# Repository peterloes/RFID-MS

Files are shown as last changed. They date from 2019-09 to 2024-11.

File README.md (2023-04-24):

# RFID Management System RFID-MS
 
Authors: Loës P., Skripsky P., Kempenaers B. (2019) 

### Platform for animal observation 

An efficient system to monitor animal behaviour in wildlife
as well as in laboratory settings.

-	Compatible with different RFID systems and triggers
-	Low power consumption and specific data collection lead to long lasting collection periods
-	Applicable world-wide due to its compatibility with different types of radio clock receivers 
-	High observation quality through low disturbance of the animals

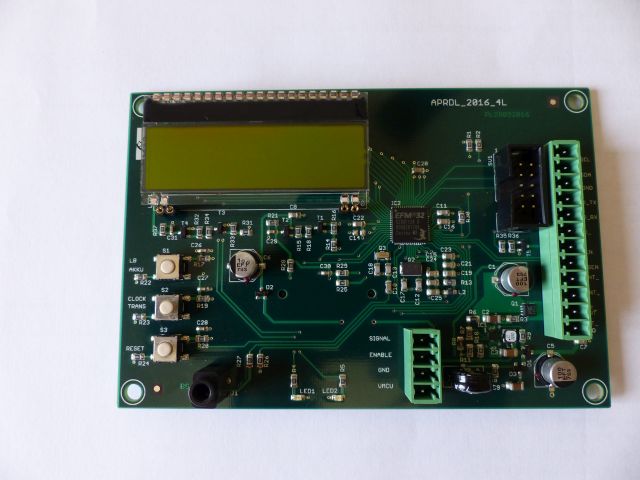
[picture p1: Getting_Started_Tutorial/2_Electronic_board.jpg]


- Time Synchronization with atomic clock once a day to ensure optimal data quality
- Current Control twice a day
- Forecast for Battery-Change implemented
- Energy Bypass so that Date and Time are maintained even when changing battery
- Hyperterminal Output to get real-time data to the computer/laptop
- Low-Power Device:sleep: 40µA@12V awake: 12mA@12V

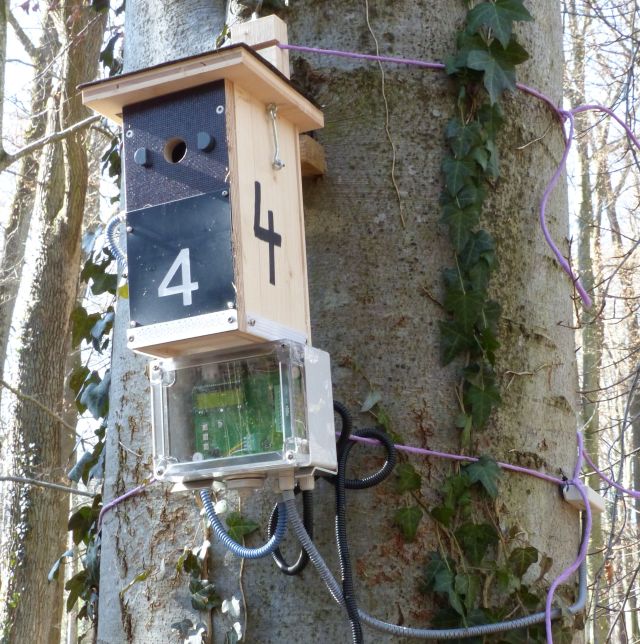
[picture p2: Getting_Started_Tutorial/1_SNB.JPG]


SmartNestBox Application:

https://github.com/peterloes/RFID-MS/blob/master/Getting_Started_Tutorial/1_poster_overview_2.pdf

Raw data on SD Card:

https://github.com/peterloes/RFID-MS/blob/master/Getting_Started_Tutorial/6_rawdata_BOX0001.TXT

Optional components:

https://github.com/peterloes/Light_Barrier

https://github.com/peterloes/Booter_RFID-MS_MOMO_TAMDL

https://github.com/peterloes/Clock_receiver_RFID-MS_MOMO_TAMDL

Manufacture:

https://github.com/peterloes/RFID-MS/blob/master/Getting_Started_Tutorial/5_Supplier.txt

C is the Greenest Programming Language

To achieve its power and energy-efficiency features, EFM32 products utilize ultralow active and idle power,
fast wakeup and processing times, and most important, the ability to intelligently interact with peripherals
and sensors autonomously without waking up the CPU and consuming more power.

[\[paper\]](https://www.sciencedirect.com/science/article/pii/S0003347223000258?via%3Dihub)
Data on the Start and End of Activity.
All 277 nestboxes were equipped with a monitoring system that
automatically recorded each nestbox visit of a PIT-tagged individual.

https://www.mpg.de/14346664/0113-verh-060830-first-come-first-bred

https://www.mpg.de/14345523/0113-verh-060830-wer-zuerst-kommt-bruetet-zuerst

EXTENSION:

Smart nest-box with long range RFID reader and external light barrier.

https://github.com/peterloes/RFID-MS/blob/master/Getting_Started_Tutorial/3_SNB_LR_LB.jpg

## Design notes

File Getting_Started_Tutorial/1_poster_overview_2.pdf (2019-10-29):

### Radio frequency identification (RFID) Management System

A Novel Technology for Collecting Animal Behavioural Data

Peter Loës & Peter Skripsky Department Kempenærs

Max-Planck-Institut
für Ornithologie

8,3 mm

Standard recording (bird entering nest box):

20190122-170542.326 LBO:ON 20190122-170542.326 RFID is powered ON 20190122-170542.484 LBI:ON 20190122-170542.670 Transponder: 6140000000008001
20190122-170543.870 LBO:off 20190122-170543.924 LBI:off 20190122-171143.000 RFID is powered off

RFID tag/transponder:

Uses of the APRDL:
- Reproductive behavior (e.g. incubation and brooding rates, feeding rates, etc.)
- Individual dispersal for adults and fledglings
- Survival or return rates
- Breeding site selection
- Social interactions (e.g. social networks at feeders)

Benefits of using APRDL over traditional methods

(visual observations and camera traps):
- No observer biases and not affected by low visibility
- Autonomous – requires minimal battery and SD card changes
- Only active during events (e.g. bird entering a nest box) → does not need time-consuming processing like camera traps
- Allows for 24/7 data collection, and large data sets with high accuracy
- Compatible with any species that can be equipped with a RFID tag

Specifications:
- Low power device → inactive current mode = 40µA (0,040mA)
- Useful for wild populations and laboratory experiments
- Compatible with different RFID readers and external triggers (Light barriers or infrared detectors)
- Can be used with different radio clock receivers (e.g. Germany 77,5 kHz, UK and USA 60 kHz, and China 68,5 kHz)
- Reliable in harsh environments (-40°C – 60°C)
- Used with Short Range readers (3,3V@0,22A)
- 12V battery pack

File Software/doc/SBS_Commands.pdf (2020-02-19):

# Projekt U-BMS2-4

# SBS-

# Commands

# SBS Commands

Device Address | | | | | | 0x0A
ManufacturerAccess | | | | | | 0x00

Read word

RemainingCapacityAlarm | 0x01

Read word
Rückgabe des remainingCapacityAlarm-Wertes in [mAh].

Wenn die Restkapazität(remainingCapacity) kleiner als der Wert vom RemainingCapacityAlarm ist, sendet die Batterie eine Alarmwarnung zum Host. Der RemainingCapacityAlarm-Flag im Battery-Status wird gesetzt.

RemainingTimeAlarm | 0x02

Read word
Rückgabe des remainingTimeAlarm -Wertes in [min].

Wenn die durchschnittliche Entladezeit des Akkus(AverageTimeToEmpty) kleiner als der Wert vom
RemainingTimeAlarm | ist, | sendet | die | Batterie | eine | Alarmwarnung | zum | Host. | Der
RemainingTimeAlarm-Flag im Battery-Status wird gesetzt.
Battery Mode | | | | | | 0x03

Read word

Bit | Beschreibung

### 12 BALANCING CELL3

### 11 BALANCING CELL2

### 10 BALANCING CELL1

### 6 BALANCING CELL4

### 5 Deep Under Voltage recovery(DUVRD) Bit vom FET Control and Status-Register

(FCSR)

### 4 Current Protection Status (CPS) Bit vom FET Control and Status-Register (FCSR)

### 3 Discharge FET (DFE) Bit vom FET Control and Status-Register (FCSR)

### 2 Charge FET (CFE) Bit vom FET Control and Status-Register (FCSR)

CoreTemperature | 0x08

Read word
Die aktuelle Chip-Temperatur in [°K]
Voltage | 0x09

Read word
Die gesamte Akkuspannung in [mV]
BatteryCurrent | 0x0A

Read word
Der aktuelle Strom in [mA], der aus bzw. in den Akkupack durchfließt.
BatteryAverageCurrent | 0x0B

Read word
Der durchschnittliche Strom des Akkupacks in [mA]
RelativeStateOfCharge | 0x0D

Read word
Der relative Ladezustand des Akkupacks in [%]
AbsoluteStateOfCharge | 0x0E

Read word
Der absolute Ladezustand des Akkupacks in [%]
RemainingCapacity | 0x0F

Read word
Die Restkapazität des Akkupacks in [mAh]
FullChargeCapacity | 0x10

Read word
Rückgabe der vollen Ladekapazität in [mAh]
RunTimeToEmpty | 0x11

Read word
Die Ladezeit in [min]
AverageTimeToEmpty | 0x12

Read word
Die durchschnittliche Entladezeit [min]
AverageTimeToFull | 0x13

Read word
Die durchschnittliche Ladezeit in [min]

ChargingCurrent | 0x14

Read word
Der Ladestrom in [mA]
ChargingVoltage | 0x15

Read word
Die maximale Ladespannung in [mV]
Battery Status (flags) | 0x16

Read word

Bit | Beschreibung

### 15 Over Charged Alarm

Überprüfung des chargingProhibited-Flags

### 14 Terminate Charge Alarm

Überprüfung des voltageTooHigh-Flags

### 12 Over Temp Alarm

Überprüfung des cellTemperatureTooHigh -Flags

### 11 Terminante Discharge Alarm

Dieses Bit wird gesetzt, wenn die Restkapazität unter dem definierten Wert von SBS_TERMINATE_DISCHARGE_LIMIT (Standard 5mAh) liegt. Wenn ein Ladegerät erkannt wird, wird dieses Bit gelöscht.

### 10 Battery Protection Triggered

Dieses Bit wird gesetzt, wenn die Batterieschutz-Hardware die FETs ausschaltet.

### 9 Remaining Capacity Alarm

Dieses Bit wird gesetzt, wenn die Restkapazität weniger als der definierte Wert des Restkapazität-Alarms(RemainingCapacityAlarm) ist.

### 8 Remaining Time Alarm :

Wenn die durchschnittlische Entladezeit (AverageTimeToEmpty) kleiner als der definierte Wert des Entladezeit-Alarms (RemainingTimeAlarm) ist, wird dieses Bit gesetzt.

### 7 Initialized

Dieses Bit wird gesetzt, wenn die Initialisierung erfolgreich abgeschlossen ist.

### 6 Discharging

Dieses Bit wird gesetzt, wenn ein Entladestrom fließt.

### 5 Fully Charged

Dieses Bit wird gesetzt, wenn die Batterie vollständig geladen ist. Wenn ein Entladestrom aus der Batterie fließt, der höher als der Standby-Stromwert ist, wird dieses Bit gelöscht.

### 4 Fully Discharged

Dieses Bit wird gesetzt, wenn die Restkapazität der Batterie bzw. die Zellenspannung sehr niedrig ist. Wenn der relative Ladezustand über 20% steigt, wird dieses Bit gelöscht.

ChargerCycleCount | 0x17

Read word
Die Anzahl der Ladezyklen
DesignCapacity | 0x18

Read word
Die Nennkapazität in [mAh]
DesignVoltage | 0x19

Read word
Die Nennspannung in [mV]
SpecificationInfo | 0x1A

Read word
Die Spezifikation-Info (Version und Revision-Nummer)
ManufactureDate | 0x1B

Read word
Das Herstellungsdatum
SerialNumber | 0x1C

Read word
Die Seriennummer
ManufacturerName | 0x20

Read Block
Der Name des Herstellers
DeviceName | 0x21

Read Block
Der Name des Gerätes
DeviceChemistry | 0x22

Read Block
Die chemische Bezeichnung des Gerätes
ManufacturerData | 0x23

Read Block
Die Herstellerdaten
ShuntResistance | 0x2A

Read word
Der Wert des Shunt-Widerstands in [µOhm]

CellsInSeries | 0x3C

Read word
Anzahl der verwendeten Zellen in Serie
OverCurrentReactionTime | 0x3D

Read word
Überstrom Reaktionszeit Stufe 1
OverCurrentCharge | 0x3E

Read word
Überladestrom Stufe 1
OverCurrentDischarge | 0x3F

Read word
Überentladestrom Stufe 1
HighCurrentReactionTime | 0x40

Read word
Überstrom Reaktionszeit Stufe 2
HighCurrentCharge | 0x41

Read word
Überladestrom Reaktionszeit Stufe 2
HighCurrentDischarge | 0x42

Read word
Überentladestrom Stufe 2
VoltageCell4 | 0x44

Read word
Rückgabe der Spannung der Zelle 4 in [mV]
VoltageCell3 | 0x45

Read word
Rückgabe der Spannung der Zelle 3 in [mV]
VoltageCell2 | 0x46

Read word
Rückgabe der Spannung der Zelle 3 in [mV]

VoltageCell1 | 0x47

Read word
Rückgabe der Spannung der Zelle 1 in [mV]
CellMinVoltage | 0x54

Read word
Die minimale Zellenspannung in [mV]
CellMaxVoltage | 0x55

Read word
Der Wert der maximalen Zellenspannung in [mV]
CellPowerOffVoltage | 0x55

Read word
Der Wert der Zellenspannung in [mV], bei der das BMS in den PowerOffModus geht

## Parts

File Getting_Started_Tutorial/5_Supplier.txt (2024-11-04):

Active antennas
DCF77 Empfänger AASV DCFn PON/Ri/1m Aktivantenne SV DCFn 

HKW-Elektronik GmbH
Jörg Schneider

Eisenacher Str. 42 b
99848 Wutha-Farnroda / Thür.
Germany
Phone:  +49 (0)36921 3080 130
mailto:    schneider@hkw-elektronik.de
www.hkw-elektronik.de

Lightbarriers for front plate nestbox
Doppel - Lichtschranke Art.Nr. P00700 (Lichtschranken in Frontplatten):

SWISSSENSOR AG
Geschäftsleitung Hermann Beer

Steinacherstrasse 4
CH-9327 Tübach
Germany
Tel. +41(0)71 845 24 24
mailto:beer@swisssensor.ch
www.swisssensor.ch

Lithium Ionen rechargeable battery pack
Art.Nr. 60.16294 Panasonic NCR 18650GA 4S2P
14,4Volt 6900mAh inklusive SMBus Kabel je. 150mm 

DYNAMIS Batterien GmbH
Josef Pfeil

Brühlstraße 15  D- 78465 Dettingen / Konstanz
Tel. +49 (0) 75 33/93 669-15
mailto:josef.pfeil@dynamis-batterien.de
www.dynamis-batterien.de

RFID reader
Nanomodule Multi 125LV A/1.11 (T3NM-LV) 125kHz +/-0,5% Art.Nr. ART10413
ANT002 Rundspule 47mm, 490µH Art.Nr. ART 10668

Elatec GmbH
Felix Ellspermann

Zeppelinstr. 1
82178 Puchheim 
Germany
Tel: +49 89 552 9961 120
mailto: f.ellspermann@elatec.com
www.elatec-rfid.com

Small sized transponder, not uniqued.
GlassTag 1,41x8,3mm EM4305 134kHz

Programming required for transponders.

Rasmus Forntheil
Product Manager Animal ID
RBIS Europe, Smartrac Specialty GmbH

e: rasmus.forntheil@eu.averydennison.com
t: +49 (0) 2265 9919-14  |  m: +49 (0) 173 5688184
Gewerbeparkstr. 10, 51580 Reichshof-Wehnrath, Germany

Internet: https://www.averydennison.com/en/home.html

Supplier of all Electronic Boards

Top-Print Electronic GmbH
Oskar Schmid

Rosenheimer Landstr. 129a
85521 Ottobrunn
Germany
Tel.: +49-89-60668047
Fax: +49-89-60668049
mailto: info@top-print.eu
https://www.leiterplatten-muenchen.de/

Protective coating with Schmelzharz Bectron MR3404

KC – Kunststoff- Chemische Produkte GmbH
Holger Sarau-Burghardt

Leonberger Straße 86 
DE 71292 Friolzheim
phone: +49 (0)7044 9425 13
e-mail: h.sarau-burghardt@kc-produkte.com
http: www.conformalcoating.de

Industrial SD Cards ATP 2GB
https://www.atpinc.com/products/industrial-sd-cards

FTDI Chip cable (3.5mm Audio Jack to USB)
TTL-232R-3V3-AJ

Housing
https://www.spelsberg.de/industrieleergehaeuse/glatt-mit-befestigungsnocken/20100701/
TG PC 1612-9-to
Artikelnummer: 20100701 | Maße: 162 x 122 x 90 mm
Leergehäuse IP66 / IP67 Polycarbonat

Docklight RS232 Terminal / RS232 Monitor
https://docklight.de/information/

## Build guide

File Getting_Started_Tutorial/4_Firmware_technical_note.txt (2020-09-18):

APRDL (code name SNB_Heaven) is an application to control an intelligent
nest box (SNB = Smart Nest Box).  It consists of the following components:

APRDL_2020

Version 1.2
- Added support for battery controller TI bq40z50.
  LogBatteryInfo: Removed SBS_ManufacturerData.
  Display SBS_RunTimeToEmpty in days/hours/min.
  Display SBS_SerialNumber as hex value.
- Corrected decoding of Short-Range(SR) RFID Reader transponder ID
- Added Power Fail Logic
- Added Interrupt Priority Settings

Version 1.1

- ExtInt.c - External interrupt handler.
- Keys.c - Key interrupt handling and translation.
- AlarmClock.c - Alarm clock and timers facility.
- DCF77.c - DCF77 Atomic Clock Decoder
- clock.c - An implementation of the POSIX time() function.
- LCD_DOGM162.c - Driver for the DOGM162 LC-Display.
- Display.c - Display manager for LCD.
- LightBarrier.c - Interrupt logic for the outer and inner light barrier,
  enables the RFID reader.
- RFID.c - RFID reader to receive transponder IDs.
- BatteryMon.c - Battery monitor, periodically reads the state of the
  battery via the SMBus.
- LEUART.c - The Low-Energy UART can be used as monitoring and debugging
  connection to a host computer.
- microsd.c - Together with the files "diskio.c" and "ff.c", this module
  provides an implementation of a FAT file system on the SD-Card.
- Logging.c - Logging facility to send messages to the LEUART and store
  them into a file on the SD-Card.

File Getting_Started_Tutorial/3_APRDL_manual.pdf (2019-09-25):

## Max-Planck-Institut für Ornithologie

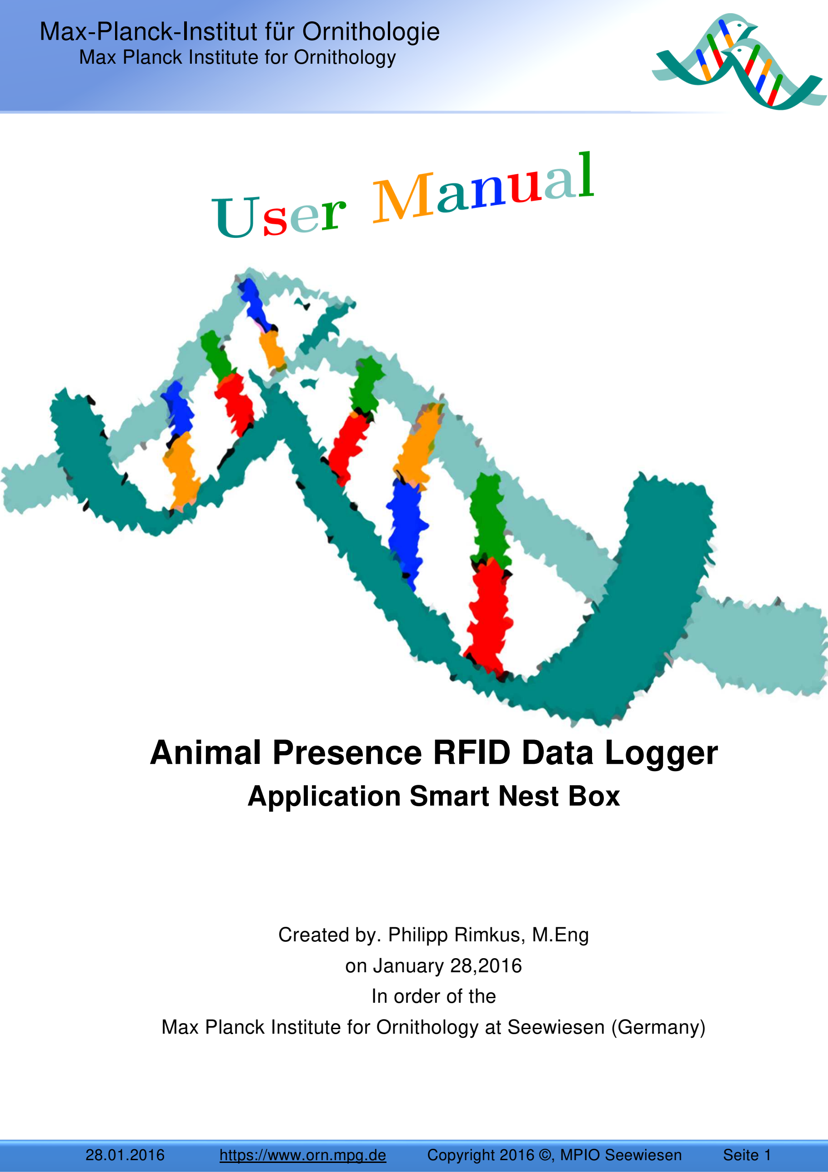
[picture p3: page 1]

Max Planck Institute for Ornithology

28.01.2016 | https://www.orn.mpg.de | Copyright 2016 ©, MPIO Seewiesen | Seite 1

# Animal Presence RFID Data Logger

## Application Smart Nest Box

Created by. Philipp Rimkus, M.Eng on January 28,2016
In order of the
Max Planck Institute for Ornithology at Seewiesen (Germany)

Disclaimer und Copyright

28.01.2016 | https://www.orn.mpg.de | Copyright 2016 ©, MPIO Seewiesen | Seite 2

## Disclaimer

The Animal Presence RFID Data Logger is to be used only as that described in this document. Any other method of usage is not permitted. If damage occurs due to incorrect usage, the manufacturer of the Animal Presence RFID Data logger is not liable.

## Copyright ©

The Copyright for this user manual remains with the manufacturer. Text and figures meet the latest technical status at the time of publication. Subject to change. The content of the user manual shall not affect any claims of the purchaser. The editor also welcomes suggestions of any possible improvements you may have or whether any errors are encountered.

Abkürzungsverzeichnis

28.01.2016 | https://www.orn.mpg.de | Copyright 2016 ©, MPIO Seewiesen | Seite 3

## List of abbreviations

SNB | Smart Nest Box
LBO | Light Barrier Outer
LBI | Light Barrier Inner
RFID | radio-frequency identification
EFM | Energy Friendly Microcontroller
PCB | printed circuit board
DCF | D for Deutschland (Germany), C for long-wave transmitter, F due to the vicinity to the Town Frankfurt
LCD | Liquid Crystal Display
ARM | Advanced RISC Machines
SD-CARD | Secure Digital Memory Card
PIT | Passive Integrated Transponder
LEUART | Low Energy Universal Asynchronous Receiver/Transmitter
USB | Universal Serial Bus

System Overview

28.01.2016 | https://www.orn.mpg.de | Copyright 2016 ©, MPIO Seewiesen | Seite 4

## System Overview

## General Description of Functions

The Animal Presence RFID Data Logger has been developed to record the behaviour of animals. When animals are equipped with transponders, they can then be identified by a reading device. Every animal equipped with a transponder can be identified individually. Whenever the individual passes a short tube containing the RFID Reader, the transponder code, date and time are saved on a SD-card.

The Animal Presence RFID Data Logger is designed for flexible, mobile operation in field. Therefore, the Data Logger uses rechargeable lithium-ion batteries to supply the electrical energy.

The use of electronic devices in the field and nature requires special features in order to operate correctly. Special developments are needed in order to cope with changes in ambient temperature, humidity, pressure and when the electrical power grid is unavailable. However, such developments can be time-consuming and cost-intensive.

Video recordings and visual observations have long been used by biologists to document behaviour of animals at their nests, and answer questions about territory, distribution and reproductive behaviour. However, these methods are time consuming, often inexact, and cannot be used when visibility is low (e.g. at night).

In a population of animals tagged with RFID devices the Animal Presence RFID Data Logger (APRDL), can detect, record and identify different individuals. This technology can be used for any species as long as the RFID tag (which is similar in size to a grain of rice) can be attached to the animal. The APRDL can be placed in any area where individuals are expected to frequent, such as a food source, nest or roosting area.

One major application of the APRDL is the Smart Nest Box, which is a wooden structure used by birds to rear their young. The APRDL records the presence of RFID-tagged adults, providing data on questions on many aspects of reproductive behaviour, including nest site selection, incubation and feeding behaviours. If the young are also equipped with RFID tags, behaviour, fledging data and movement in an out of the nest can also be recorded.

System Overview

28.01.2016 | https://www.orn.mpg.de | Copyright 2016 ©, MPIO Seewiesen | Seite 5

A key strength of the APRDL is that it runs autonomously, and requires only periodic battery and memory card changes. This allows for data collection over long periods of time with little effort, making the APRDL ideal for use in remote areas. It also allows data to be collected simultaneously at many sites without requiring the presence of a technician. During the development, special attention was paid developing an energy saving operation, so that a battery pack would only have to be changed every two weeks during periods of very high activity levels of the Animal Presence RFID Data Logger. The SD cards used have enough memory space to save data for several months of data collection. These low operating expenses makes the Animal Presence RFID Data Logger ideal for use in isolated locations without grid connection.

Another strength of the APRDL is how the data is recorded: the output of the APRDL is only the events (e.g. the time, date, and the individual present). This output is simple to work with, and does not require time-consuming processing, unlike video recordings where each video must be watched in order to document events. Thus the APRDL allows for easy collection of large amounts of data, making it easier to increase sample size with lower effort and higher accuracy.

Biological data is optimally collected when disturbance to the animal’s behaviour is minimised. As the APRDL is automated and requires only occasional battery and SD card changes, large volumes of data can be collected with little disturbance. It is also more accurate than many other methods of recording animal presence and identifying individuals, such as re-sighting colour bands or other markings, as these methods are prone to mistakes caused by poor visibility and human error.

Currently, the APRDL is being used on animals smaller then 70mm, however this technology could be adapted for use in any animal that can be marked with an RFID and returns to a specific area where the reader is located.

Some examples of potential uses of the APRDL

- nest boxes of birds
- bird feeders
- roosting boxes of bats
- dens of burrowing mammals or birds (i.e. rodents, badgers, rabbits, sea-

birds)
- fish such as pacific salmon that return to a stream to breed
- fish farms

System Overview

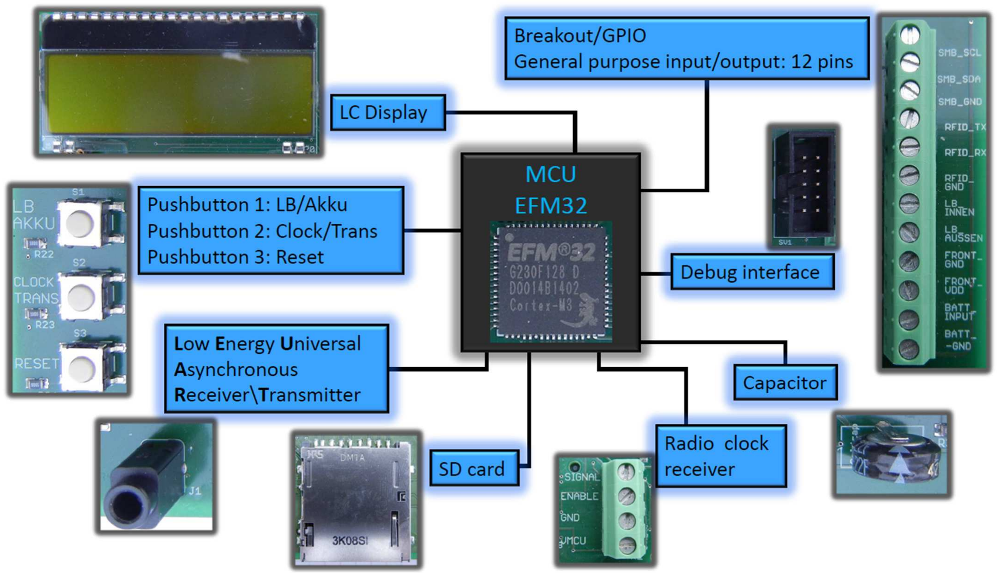
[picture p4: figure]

28.01.2016 | https://www.orn.mpg.de | Copyright 2016 ©, MPIO Seewiesen | Seite 6
- snake and reptile research
- bird movement and range

The APRDL can be used to collect data on many types of animal behaviour. Some of these include:

- Reproductive behaviours, such as incubation timing, feeding trips and the

duration of parental care.
- Dispersal and range size (the movement of animals within an area).
- Survival and return rates of individuals to an area.
- Selection of nesting or roosting locations

## System configuration main circuit board

The Smart Nest Box application of the Animal Presence RFID Data Logger was developed over several years. After five years of development a relatively reliable and efficient version was completed, which is described comprehensively in this manual. Additional detailed information, particularly concerning the electronic configuration, can be found in the datasheet for the Animal Presence RFID Data Logger.

### 1.2.1 Block diagram

System Overview

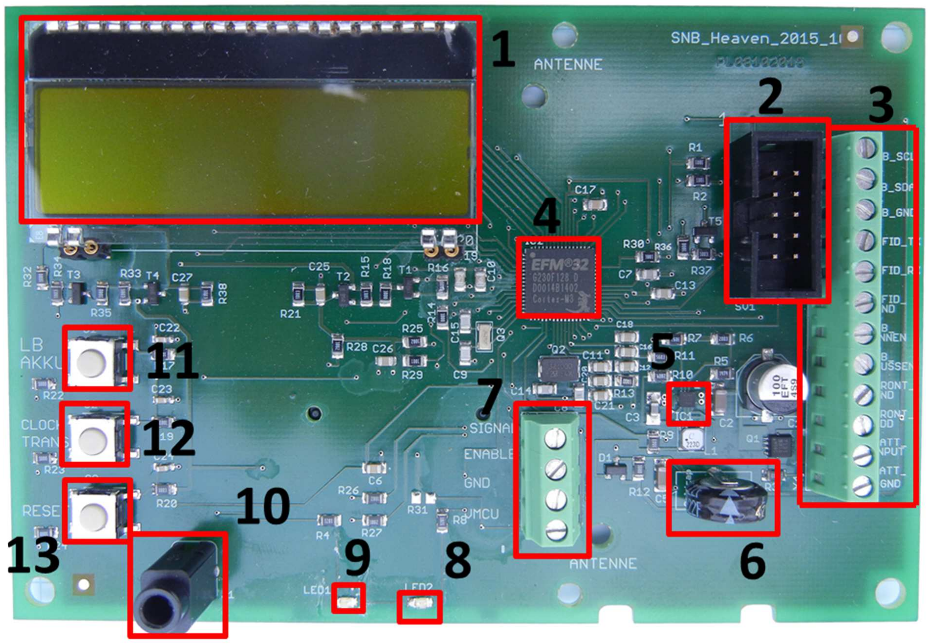
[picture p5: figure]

28.01.2016 | https://www.orn.mpg.de | Copyright 2016 ©, MPIO Seewiesen | Seite 7

### 1.2.2 Hardware Illustration

1. | LC Display | 8. | LED 2
2. | Debug interface | 9. | LED 1
3. | Connecting terminal for periphery | 10. | LEUART connector
4. | EFM32G230 | 11. | Pushbutton for battery indicator
5. | Down converter | 12. | Pushbutton for radio clock display
6. | Capacitor | 13. | Reset push button
7. Connecting terminal for the radio | clock

System Overview

28.01.2016 | https://www.orn.mpg.de | Copyright 2016 ©, MPIO Seewiesen | Seite 8

### 1.2.3 EFM32 microcontroller

A microcontroller is a small computer (SoC) on a single integrated circuit containing a processor core, memory, and programmable input/output peripherals. Program memory in the form of Ferroelectric
RAM, NOR flash or OTP ROM is also often included on the chip, as well as a typically small amount of RAM. Microcontrollers are designed for embedded applications, in contrast to microprocessors used in personal computers or other general purpose applications consisting of various discrete chips

The EFM32 MCUs by Energy Micro are the world’s most energy-friendly microcontrollers. With a unique combination of the powerful 32-bit ARM Cortex-M3, innovative low energy techniques, short wake-up time from energy saving modes, and a wide selection of peripherals, the EFM32G microcontroller is well suited for any battery operated application as well as other systems requiring high performance and low-energy consumption. EFM stands for Energy Friendly Microcontrollers. The ARM Cortex-M3 processor has several energy modes that can be quickly switched back and forth between them. It is possible to connect several peripheral devices. The ARM Cortex-M3 processor is developed by Energy Micro and has been bought by Silicon Labs.

Within the Animal Presence RFID Data Logger the EFM32G230 microcontroller is used with 128 KB Flash Memory, 16 KB RAM Memory and 32 MHz.

The EFM32 series is also known as “Gecko” by the developer, as these animals consume only 10% of the energy used by a mammal of similar size.

The EFM32 microcontroller based on the ARM Cortex processor is well suited for energy saving applications such as:

- Electricity-, gas- and water-meters
- factory automation and building automation systems
- alarm and security technology

System Overview

28.01.2016 | https://www.orn.mpg.de | Copyright 2016 ©, MPIO Seewiesen | Seite 9

Energy Micro states that benchmark measurements with other leading energy saving MCU’s, found that the EFM32-MCU consumes only a quarter of the energy consumed by the other 8-, 16-, or 32-bit-MCU’s.

The EFM32G230 contains a kind of UART-interface for communication with other systems, this is especially designed for energy saving. The interface is referred to as LEUART-interface. LEUART is a serial interface, a kind of bus system. Through the LEUART-interface, a jack connector and a USB cable can be used to establish a connection to a computer.

### 1.2.4 Debug Interface (DBG)

The debug interface software is stored on the microcontroller flash memory. Only after the flash memory contains this information, the hardware can be operated. The connection is either realised directly with a USB cable to the debug interface or with a debugging probe. If the connection is realized directly through the USB cable only HEX files and BIN files can be transferred.

### 1.2.5 Liquid Crystal Display (LCD)

This kind of display screen utilizes liquid crystals, which influence the polarization direction of light when a certain amount
of electrical voltage is applied.

LCD’s consist of segments which can independently change their transparency. This is done by a change in the orientation of each segment of the liquid crystals when an electrical voltage is applied. This then changes the permeability for polarized light, which is created by a
backlight.

In the Smart Nest Box application of the Animal Presence RFID Data Logger, the LCD shows the results depending on which buttons are pressed, as described in chapter 1.2.7.

System Overview

28.01.2016 | https://www.orn.mpg.de | Copyright 2016 ©, MPIO Seewiesen | Seite 10

### 1.2.6 SD Memory Card Connector

The data from the RAM memory is stored in form of TXT files on the SD-card, this is located in the SD Memory Card Connector. The size of the memory influences the energy consumption; the smaller the memory size is, the smaller the energy consumption. Therefore, it is recommended for the Animal Presence RFID Data Logger to use the smallest possible SD memory size of 2 GB. Memory sizes are supported from 2 GB to 32 GB.

### 1.2.7 Buttons

Three pushbuttons are installed on the mainboard of the Animal Presence RFID Data Logger. A LB Akku button, a Clock Trans button and a reset button

- LB Akku: Displays the status of the light barriers and

the status of the accumulator on the LCD.
- Clock Trans: Displays the date, time and the number of

the most recent transponder to enter the Smart Nest Box.
- Reset: Restarts the Animal Presence RFID Data Logger.

### 1.2.8 Capacitor

A capacitor (German “Kondensator”) is a passive electric component with the ability to store electrical charge and electrical energy in an electrical field.

When the electrical power supply through the accumulator for the Animal Presence RFID Data Logger
is missing, the capacitor ensures an alternate power supply. The capacitor is charged when the accumulator supplies energy to the system. This allows energy to be obtained for a certain time from the capacitor if it is required.

System Overview

28.01.2016 | https://www.orn.mpg.de | Copyright 2016 ©, MPIO Seewiesen | Seite 11

A Gold Cap is a double-layered capacitor, developed by Panasonic in 1972, then in 1978 it was brought released to the market. It is often known as “super cap” by a number of manufacturers. The name “Gold Cap” is the official trade name of the capacitor, trademarked by Panasonic. Cap is the shortcut for Capacitor. The gold refers to the gold plating of these capacitors. Gold is not contained in this capacitor.

The double-layered capacitor or Gold Cap is a mixture of a battery and a conventional capacitor. It combines speed and a large energy storage to form a super capacitor. With respect to its properties, it is ordered between electrolytic capacitors and rechargeable batteries.

Some applications only become possible through double layered capacitors. Despite its large capacity, it is very small in size. The dielectric strength is not exceptionally high however, with only a few volts. Through its large capacity, the Gold Cap is present to maintain the power supply when the main energy source fails. In devices in which data storage should remain in switched off status, the Gold Cap is particularly well suited.

Life expectancy is limited from roughly 8 to 10 years. When the operating temperature is above optimal or the discharge current is high, the life expectancy and the capacity begin to decline over time. The Gold Cap most appropriate when it is rarely discharged and used with low currents.

### 1.2.9 Jack connector as interface to a PC

For the development of the Animal Presence RFID Data Logger an Interface for connection to a computer is intended. Through the data communication interface LEUART, which is provided by the
EFM32G230 out of chapter 1.2.3.

The jack connector is used to interlink the signal from the LEUART interface with a computer. Specifically, a jack connector of 3.5 mm is used, as those used in many audio applications.

### 1.2.10 Down converter

The TPS62125 from Texas Instruments, is a high efficiency synchronous step down converter optimized for low and ultra-low power applications providing up to 300 mA output current. It has a wide range of input voltages, from 3V to 17V, sup-

System Overview

28.01.2016 | https://www.orn.mpg.de | Copyright 2016 ©, MPIO Seewiesen | Seite 12

ports four cell alkaline, and 1 to 4 cell Li-Ion batteries in series configuration as well as 9V to 15V powered applications. The device includes a precise low power enabled comparator which can be used as an input supply voltage supervisor (SVS), this addresses system specific power up and down requirements.

### 1.2.11 LED’s

The Animal Presence RFID Data Logger is equipped with two LED’s, one red and one orange. The orange LED (LED 2) indicates, that something is written on the SD card. If the red LED (LED 1) flashes, this indicates that the radio clock is transmitting a signal to the MCU. If the LED 1 blinks longer than 5 minutes or flashes continuously, this indicates a malfunction.

### 1.2.12 Connector for the peripherals

At the connector for the peripheral devices, devices such as a batteries, light barriers and RFID’s are connected here. The connected cables are collected and lead out of the housing in a cable conduit. A sealing against water and moisture is present here and very important.

## System configuration secondary board with radio clock

On the mainboard a secondary board is installed, this secondary board is attached by spacers. The antenna is located on the secondary board at the DCF77 receiver module . The distance between the DCF77 receiver module and the mainboard is necessary to improve the reception quality of the antenna.

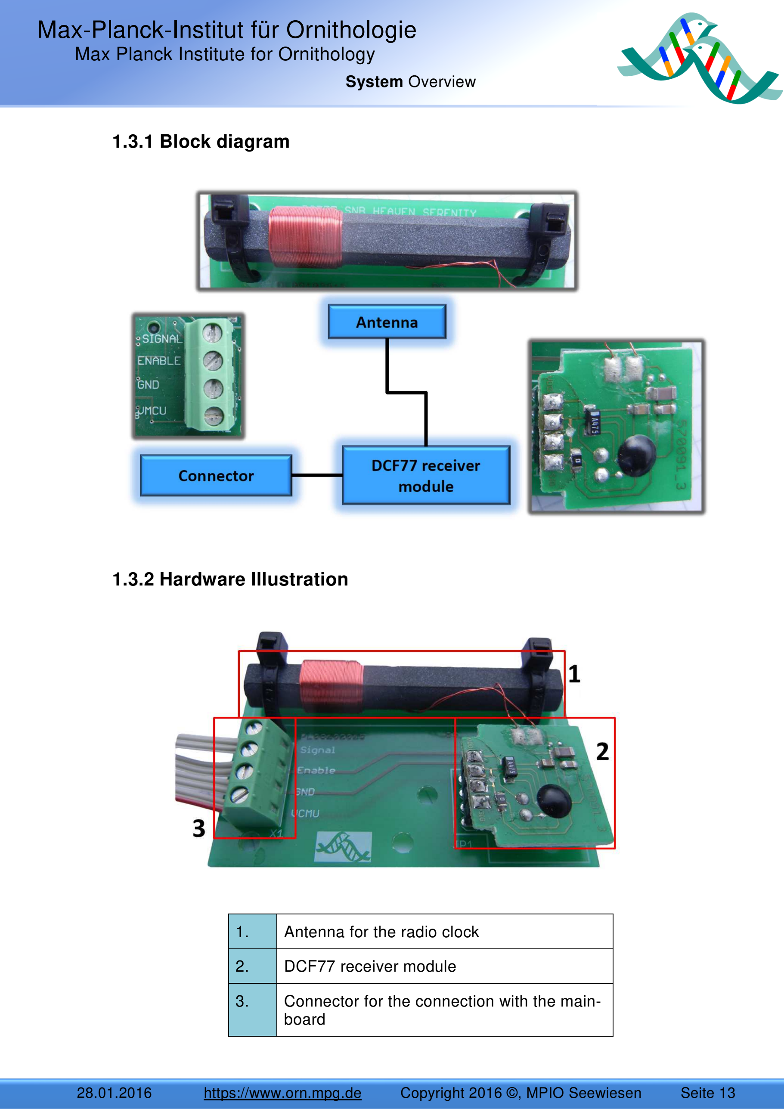
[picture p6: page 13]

System Overview

28.01.2016 | https://www.orn.mpg.de | Copyright 2016 ©, MPIO Seewiesen | Seite 13

### 1.3.1 Block diagram

### 1.3.2 Hardware Illustration

1. Antenna for the radio clock
2. DCF77 receiver module
3. Connector for the connection with the main- | board

System Overview

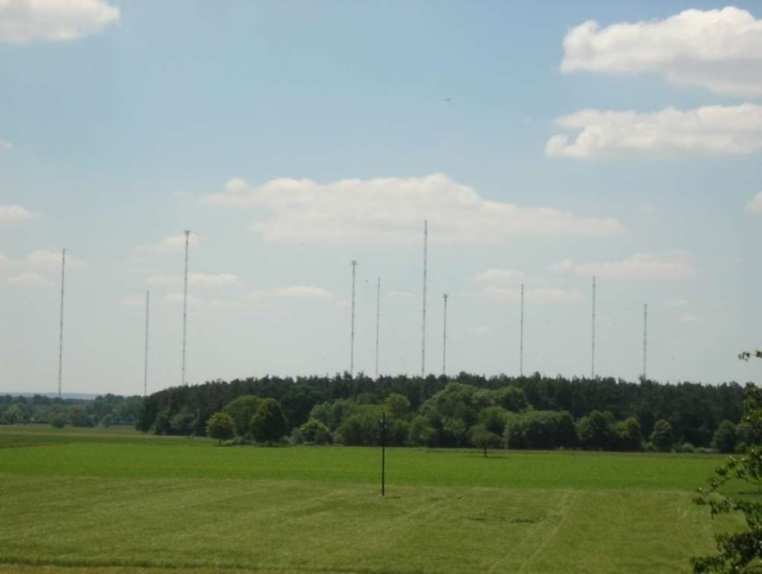
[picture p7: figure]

28.01.2016 | https://www.orn.mpg.de | Copyright 2016 ©, MPIO Seewiesen | Seite 14

### 1.3.3 Radio clock DCF (77.5KHz)

The current version of the Animal Presence RFID Data Logger features a radio clock, which works in a similar way as normal radio alarm clocks. In periodic intervals a signal to Europe from the long wave antenna in Mainflingen with a frequency of 77.5 kHz is received and synchronized. Long wave signals have been compared to short waves and medium
waves, and have a relatively high
range. So it is possible to receive
the signal from Mainflingen with a range up to 2000 km. In other continents the time signals can be also received, however with different frequencies. The radio clock is powered via an accumulator, which is also used for the other electrical consumers and is described in chapter 1.5.
countries | designation | frequency
Germany | DCF | 77.5 kHz
France | TDF | 162 kHz
China | BPC | 68.5 kHz
Japan | JJY | 40 und 60 kHz
USA | WWVB | 60 kHz
Russia | Beta | 25 kHz
England | MSF | 60 kHz

System Overview

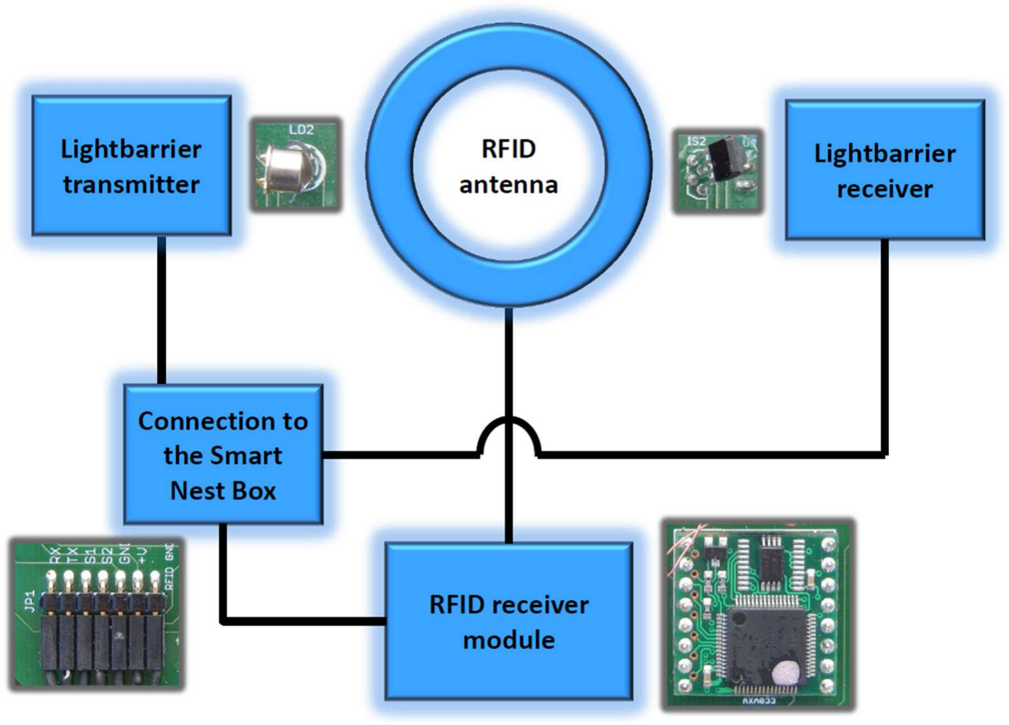
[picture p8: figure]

28.01.2016 | https://www.orn.mpg.de | Copyright 2016 ©, MPIO Seewiesen | Seite 15

## Peripheral equipment Smart Nest Box

Some peripheral devices are necessary for the operation of the Animal Presence RFID Data Logger with the Smart Nest Box application. These are the accumulator, two light barriers and an RFID reader.

### 1.4.1 Block diagram Smart Nest Box front panel

System Overview

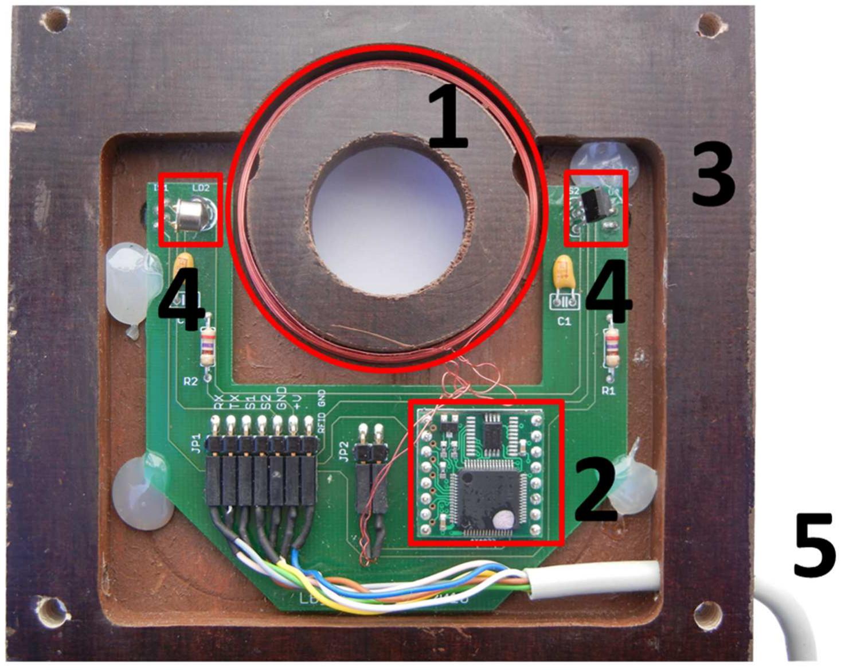
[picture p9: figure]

28.01.2016 | https://www.orn.mpg.de | Copyright 2016 ©, MPIO Seewiesen | Seite 16

### 1.4.2 Hardware illustration

The front panel may become damaged by squirrels, so much that the front panel had to be displaced. In recent versions the board and the antenna are sealed with plastic resins to avoid damages through oxidation.

1. Antenna with 70 mm diameter
2. RFID receiver module
3. Front panel of the Smart Nest Box con- | sisting of wood
4. Light barrier
5. Cable connection to the mainboard

System Overview

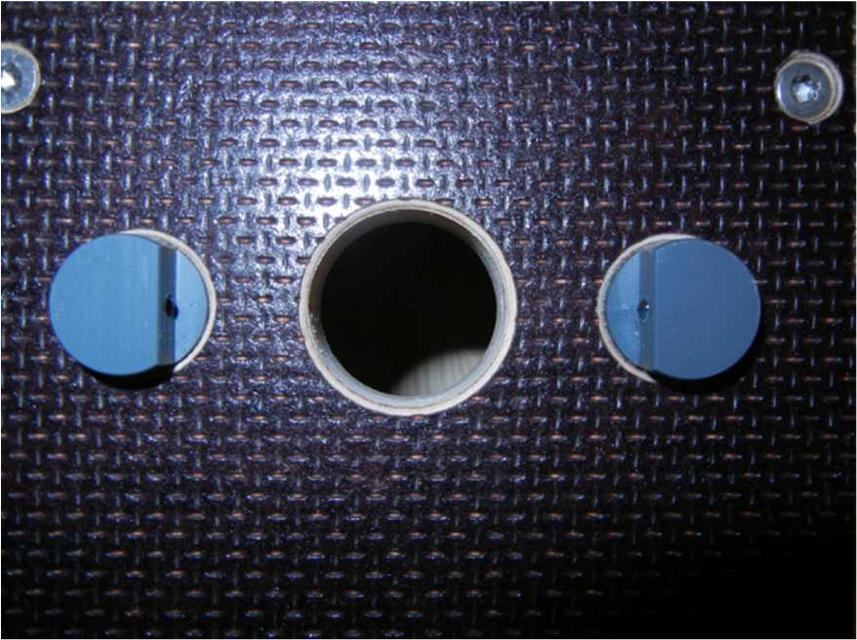
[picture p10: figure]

28.01.2016 | https://www.orn.mpg.de | Copyright 2016 ©, MPIO Seewiesen | Seite 17

### 1.4.3 Light barrier

A light barrier is an optoelectronics systems, these indicate an interruption in the beam of light and communicates this event through an electrical signal. Light barriers are composed of a beam source (transmitter) and a photodiode (emitter) to receive the beam.

In the Smart Nest Box application, the
light barriers detect the movements of the birds, including the direction of motion. On each side of the front panel there is one light transmitter and a light emitter, these detect the flight direction.

The light barriers can scan with a frequency of up to 100 Hz. The current consumption at 10 Hz is less than 30 µA (calculated). The covering of the light barriers is submitted through an
open collector output.

After the light barrier detects an object in the entrance of the Smart Nest Box, the RFID reader is activated. This needs to occur in a relatively short time, as often birds will fly very quickly through the entrance into the Smart Nest Box. If signal transmission is slower, the RFID can’t receive the transponder signal from the bird because the bird may already be out of range.

The light barriers work with adaptive selectivity, which means that pollution of the transmitter and emitter, aging or fluctuations due to temperature can be largely compensated for. This reduces the possibility of false detections for example through sunlight.

### 1.4.4 RFID

Radio-frequency identification (RFID) uses electromagnetic fields to automatically identify and track transponders attached to objects. The transponders contain electronically stored information. Passive transponders collect energy from a nearby RFID reader's interrogating radio waves. Active transponders have a local power source such as a battery and may operate at hundreds of meters from the

System Overview

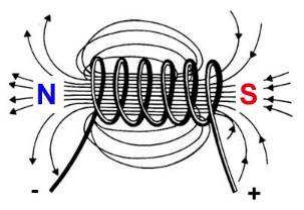
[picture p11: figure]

28.01.2016 | https://www.orn.mpg.de | Copyright 2016 ©, MPIO Seewiesen | Seite 18

RFID reader. Unlike a barcode, the transponder does not need to be within the line of sight of the reader, so it may be embedded within the tracked object.

RFID’s are also used in other areas such as electronic locks, ski passes, cashless payment transactions, electronic immobilizers and in libraries as theft protection.

In the Smart Nest Box application of the Animal Presence RFID Data Logger the transponder frequency is not exactly the same as the RFID reader frequency. The RFID Reader works with a frequency of 125 kHz and the transponder with 134.2 kHz. However, both systems are compatible and function together.

### 1.4.4.1 RFID receiver module

A RFID receiver module with a frequency of 125 kHz is used in the application Smart Nest Box. The used receiver module from Elatec is designed with a small size, small price and versatile applications.

### 1.4.4.2 RFID antenna 490µH

The used antenna has a diameter of 70 mm and is directly soldered on the RFID reader. If a voltage source is connected to the antenna, which is an air core coil and current begins to flow, an electric field is generated. The electric field is the energy source for the transponder.

If a transponder with its own antenna transmits a signal at a certain frequency, the RFID reader’s antenna collects the signal and the RFID reader transmits it further to the MCU.

System Overview

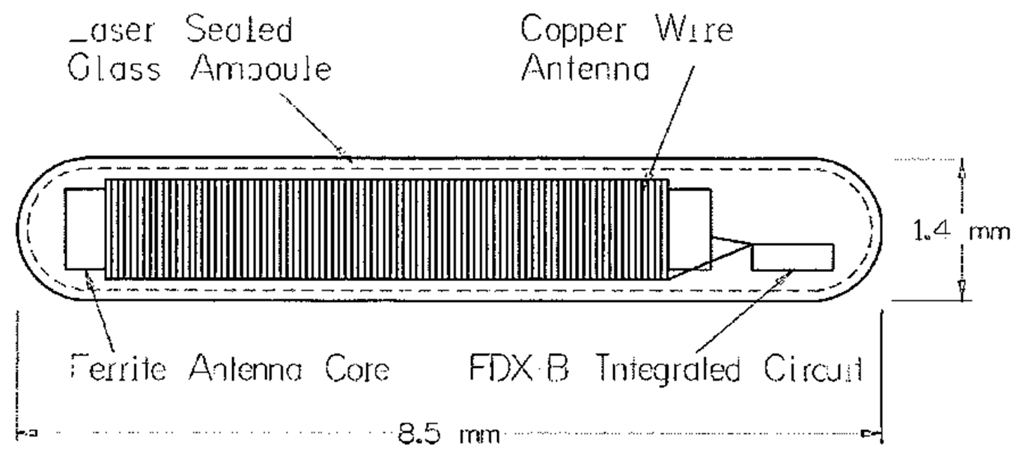
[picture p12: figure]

28.01.2016 | https://www.orn.mpg.de | Copyright 2016 ©, MPIO Seewiesen | Seite 19

### 1.4.4.3 RFID transponder

This is the highest performing RFID transponder on the market today for fish and wildlife research in an 8 mm 'skinny tag'. These transponders are encapsulated in biocompatible glass and provide 100% unique identification. Because of the small size of 8 mm x 1.4 mm
and a very low weight of only 30 mg the tagged animals are minimally affected. So it is possible to tag
even very small animals such as red ants.

The transponder contains a non-volatile flash memory. A combination of letters and numbers is stored on the flash memory during the production of the transponder.

The transponders are known as FDX-B
MINIHPT8 and are made by the company Biomark. The FDX-B indicates that the full duplex
technique is used.

In duplex mode operating systems the electric field is always present. The transponder sends its signal continuously as soon as it gets energy through the field and enters the reception area of the RFID reader. Therefore, the system works very rapidly.

System Overview

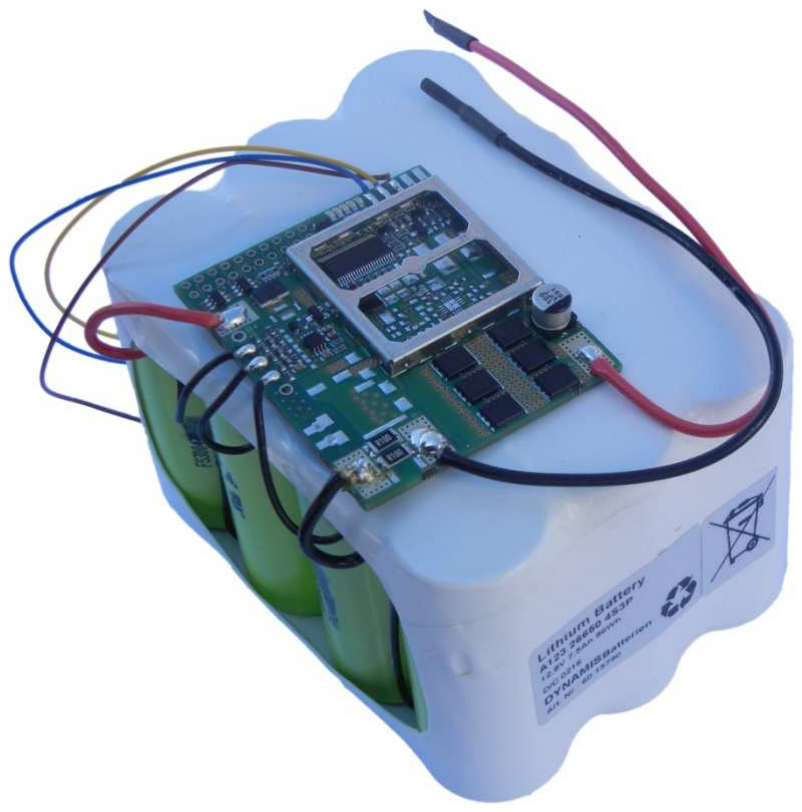
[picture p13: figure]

28.01.2016 | https://www.orn.mpg.de | Copyright 2016 ©, MPIO Seewiesen | Seite 20

## Accumulator

The lithium-ion battery from the company Dynamis Batterien supplies the Animal Presence RFID Data Logger with electrical energy. The amount of energy chosen was to ensure that there is
enough energy to supply the
Animal Presence RFID Data
Logger in a very active period for two weeks. Through the little specific energy of 108 Wh/kg the change of the accumulators is much less energy-sapping than with leadacid batteries with a specific energy of 30 – 40 Wh/kg.

The three LED’s on the accumulator’s board indicates the state of charge. One lit LED indicates that the accumulator is fully charged. Two
LED’s indicate the accumulator is halfway charged. Three
LED’s indicate an almost empty state of charge.

System Overview

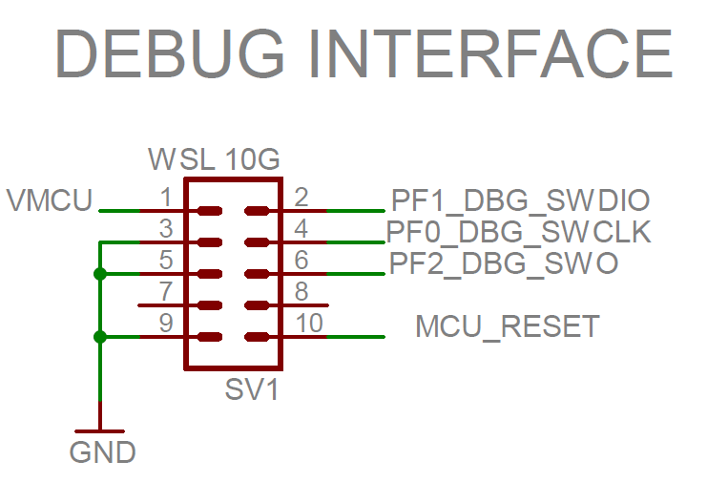
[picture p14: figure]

28.01.2016 | https://www.orn.mpg.de | Copyright 2016 ©, MPIO Seewiesen | Seite 21

## Pin assignment and connectors

### 1.6.1 Pins for debugging

### 1.6.2 Pin assignment

### 1.6.2.1 Energy supply connector

connection | designation
SV1-1 | VMCU
SV1-2 | SWDIO
SV1-3: | GND
SV1-4 | SWCLK
SV1-5 | GND
SV1-6: | SWO
SV1-7 | free
SV1-8 | free
SV1-9 | GND
SV1-10 | MCU_RESET
connection | designation | Cable color
X1-1 | BATT_GND | brown
X1-2 | BATT_INPUT | red
X1-3 | FRONT_VDD | white
X1-4 | FRONT_GND | brown
X1-5 | LB_AUSSEN | green
X1-6 | LB_INNEN | yellow
X1-7 | RFID_GND | blue
X1-8 | RFID_RX | grey

System Overview

28.01.2016 | https://www.orn.mpg.de | Copyright 2016 ©, MPIO Seewiesen | Seite 22

### 1.6.2.2 Connector for the radio clock

connection | designation
X2-1 | PD2_DCF77_Signal
X2-2 | PD1_DCF77_Enable
X2-3 | GND
X2-4 | VMCU
X1-9 | RFID_TX | pink
X1-10 | SMBUS_GND | grey
X1-11 | SMBUS_SDA | blue
X1-12 | SMBUS_SCL | yellow

System Overview

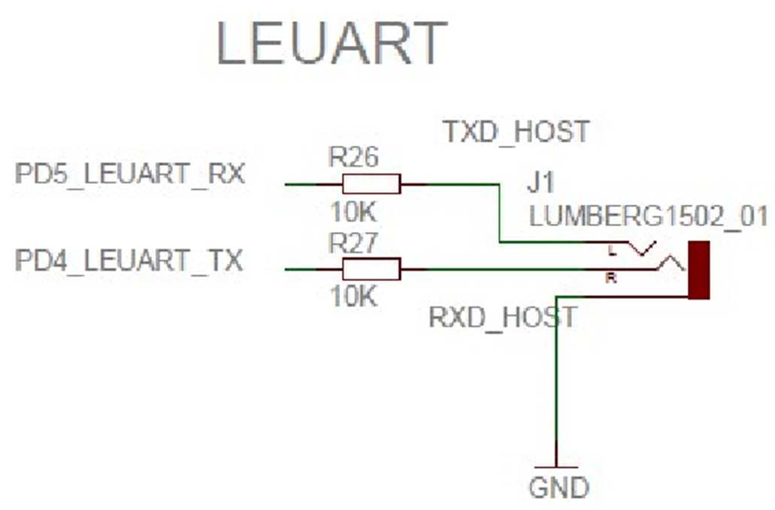
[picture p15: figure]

28.01.2016 | https://www.orn.mpg.de | Copyright 2016 ©, MPIO Seewiesen | Seite 23

### 1.6.2.3 Jack connectors for LEUART

## Housing

### 1.7.1 Housing for the main board

The housing from the main board consists entirely of opaque polycarbonate. The lid is lockable with bayonet locks which are quick and easy to use. The screws are secured from falling out and prevents loss of any screws.

connection | designation
J1 | LEUART_RX
J1 | LEUART_TX

System Overview

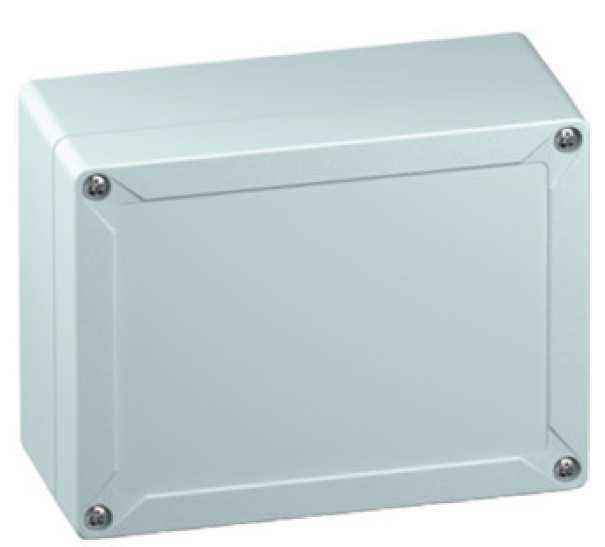
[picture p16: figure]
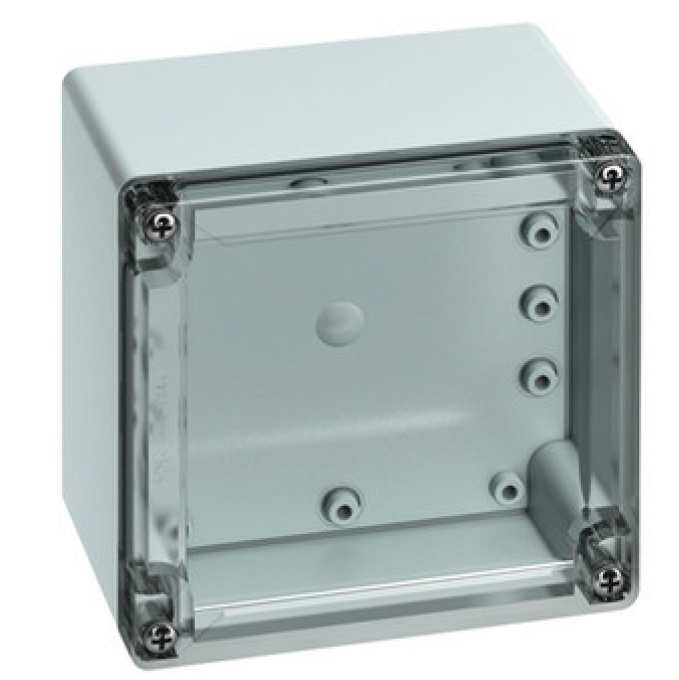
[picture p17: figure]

28.01.2016 | https://www.orn.mpg.de | Copyright 2016 ©, MPIO Seewiesen | Seite 24

### 1.7.2 Housing for the accumulator

The housing from the accumulator consists entirely of polycarbonate, with the lid being made from transparent polycarbonate so the LED’s inside may be seen without needing to open the lid. The lid is also lockable with bayonet locks. The same screws are used here and are also secured against falling out.

General working conditions

28.01.2016 | https://www.orn.mpg.de | Copyright 2016 ©, MPIO Seewiesen | Seite 25

## General working conditions

Component designation | Animal Presence RFID Data Logger
Manufacturer | MPIO http://www.orn.mpg.de/
Dimensions main board (L X B x H) | 121 mm x 81 mm x 1.5 mm
Overall temperature range | -10°C to 60°C (DCF77 and RFID) DCF is not absolutely essential -20°C to 60°C
Storage temperature range | -20°C to 60°C
Overall moisture | Relative moisture 35% to 85% (at 5°C to 35°C)

Detailed information, in particular information concerning the electrical properties can be found in the Animal Presence RFID Data Logger datasheet.

The working conditions from single devices can be found in the datasheets in chapter 7.

Energy supply

28.01.2016 | https://www.orn.mpg.de | Copyright 2016 ©, MPIO Seewiesen | Seite 26

## Energy supply

The Animal Presence RFID Data Logger is especially designed to have low energy requirements. The electrical power requirements are explained more precisely in this chapter.

The EFM32G230 has five different economical energy modes, where only two of which are used for the Animal Presence RFID Data Logger with the Smart Nest Box application. These are the Deep Sleep Mode and the Sleep Mode whereby the Sleep Mode is the Active Mode and the Deep Sleep Mode is the Inactive Mode. In these energy modes different consumers are active. The Smart Nest Box switches between the Active Mode and the Inactive Mode through light barrier activity. If the RFID reader and the light barrier detect no activity for 6 minutes the Smart Nest Box switches into the Inactive Mode again to save energy.

The energy-intensive consumers like the RFID reader are only supplied with electrical Energy when required. The RFID reader is the largest consumer of electrical energy in the Smart Nest Box application.

The electrical energy required is supplied by a lithium-ion-battery. If the energy demand and the energy storage capacity are known, the remaining range of the accumulator can be estimated.

In the following sections, the current supply and the voltage supply will be examined separately.

## Current supply

### 3.1.1 ARM Cortex Processor

From the five available modes of operation only the Deep Sleep Mode and the Sleep Mode are used.

Deep Sleep Mode or Inactive Mode

### 0.9 μA @ 3 V Deep Sleep Mode, including Real Time Clock with 32.768 kHz oscil-

lator, Power-on Reset, Brown-out Detector, RAM and CPU retention

Energy supply

28.01.2016 | https://www.orn.mpg.de | Copyright 2016 ©, MPIO Seewiesen | Seite 27

Sleep Mode or Active Mode

### 45 μA/MHz @ 3 V Sleep Mode

### 3.1.2 RFID reader

RFID on measured: 35.4mA

RFID off measured: 1.36mA

(From schematics)

### 3.1.3 Light barrier

The light barriers are always supplied with electricity independently from the two energy modes. To save energy, the status of the light barrier is not assessed continuously but 10 times per second thus with a frequency of 10 Hz. Therefore, one light barrier has a very small electrical energy demand of roughly 30 µA.

### 3.1.4 LC display

The LC display has no background light whereby results a low electrical energy demand of 0.500 mA when the LC display is switched on

If no button is pressed for 20 seconds, the LC display fades out.

Measured On 0.342mA | Measured Off: 0.016mA | (From schematics)

### 3.1.5 Radio Clock

The clock of the microcontroller is updated at a certain time in the night through the time signal DCF77 from Mainflingen. The time will be also updated when the Animal Presence RFID Data Logger is reset.

Nominal current 100µA | Quiescent current 5 µA

### 3.1.6 LED

Each LED has an electric current demand of 2 mA.

Energy supply

28.01.2016 | https://www.orn.mpg.de | Copyright 2016 ©, MPIO Seewiesen | Seite 28

### 3.1.7 Accumulator LED’s and self-discharge

LED‘s | electric current demand
Without LED | 271 µA
Only LED1 | 308 µA
LED1 + LED2 | 343 µA
LED1 + LED2 + LED3 | 384 µA

The self-discharge by lithium-ion-batteries at 20°C is less than 2% per month.

### 3.1.8 Overview of the nominal currents

This table contains the maximum current demands of the most important devices. If all are active at the same time the maximum current demand behind the down converter at 3,3 V is 51 mA and with that the power input of the Animal Presence RFID Data Logger with the Smart Nest Box application is around 0,1683 W.

devices | currents
RFID | 35.4 mA
LC display | 0.500 mA
2* LED | 2 x 2 mA
ARM Cortex M3 | 45 µA/MHz (1.44 mA)
Radio clock | 0.1 mA
Light barrier | 2 x 30 µA
Total current behind the down converter with 3.3V | 42.2 mA (When all consumers are active at the same time without down converter losses)
Total input in front of the down converter with 12.8 V | 155 mW (When all consumers are active at the same time with down converter losses)

Energy supply

28.01.2016 | https://www.orn.mpg.de | Copyright 2016 ©, MPIO Seewiesen | Seite 29

### 3.1.9 Overview of the currents in the different operating modes

| Shutoff Mode | Stop Mode | Deep Sleep | Sleep Mode | Run Mode
RFID | Not used | Not used | off | Can be on | Not used
ARM Cor-tex M3 | Not used | Not used | On | On | Not used
LCD | Not used | Not used | Can be on | Can be on | Not used
Radio clock | Not used | Not used | Can be on | Can be on | Not used
LED’s | Not used | Not used | Can be on | Can be on | Not used
Light bar-rier | Not used | Not used | On | On | Not used
Down converter | Not used | Not used | On | On | Not used
Accumu-lator board | Not used | Not used | On | On | Not used

Energy supply

28.01.2016 | https://www.orn.mpg.de | Copyright 2016 ©, MPIO Seewiesen | Seite 30
| Deep Sleep Mode (Inactive Mode) | Sleep Mode (Active Mode)
RFID | 0 | An (35.4mA)
ARM Cortex M3 | 0.9 µA | 45 µA/MHz (1.44 mA)
LCD | 1.2 mA (if on) | 1.2 mA (if on)
Radio clock | 0.1 mA (once a day, take 5 min.; also at restart) | 0.1 mA (once a day, take 5 min.; also at restart)
LED | 2 mA (2 units; if on) | 2 mA (2 units; if on)
Light barrier | 30 µA (2 units) | 30 µA (2 units)
Down converter | 13 μA | 13 μA
Total current behind the down con-verter (without down converter losses and 3.3 V) | 0.0609 mA (2 x light barriers and und MCU | 36.88 mA (RFID active, MCU active, 2 x light barriers, down converter)
Total input behind of the down con-verter (without down converter losses and 3.3 V) | 0.0609 mA x 3.3 V = 0.000201 W = 201 x 10^-6 W | 36.88 mA x 3.3 V = 0.122 W
Total input in front of the down con-verter (with down converter losses and 12.8 V) | (with η = 50%) 0.000201W/0,5 = 0.000402 W = 402 x 10^6 W | (with η = 90%) 0.122 /0.9 = 0.136 W
Total current in front of the down converter (with down converter loss-es 12.8 V) (theoretical) | (with η = 50%) 0.0314 mA | (with η = 90%) 10.6 mA
Measured total current in front of the down converter (with down con-verter losses 12.8 V) (real) | 0.070 mA = real measured Inactive Mode (connected radio clock but inac-tive, controller in Deep Sleep Mode, Gold Cap, connected LED but off, buttons, down converter) | 12.3 mA = real measured Active Mode (connected radio clock but inactive, controller, LED con-nected but off, capacitor, with-out LCD, SD card, down con-verter, light barrier, RFID on)
Accumulator board with LED‘s cur-rent demand | (0.271 mA – 0.384 mA) | (0.271 mA – 0.384 mA)
Total current with accumulator board | 0.3024 mA – 0.4154 mA | 10.87 mA – 10.98 mA
Total Input ink. accumulator board with 12.8 V (theoretical) | 0.00387 W – 0.00532 W | 0.139 W – 0.141 W
Total Input with measured value + theoretically accumulator board de-mand with 12.8 V (real) | 0.004 W – 0.0058 W | 0.161 W – 0.162 W

Energy supply

28.01.2016 | https://www.orn.mpg.de | Copyright 2016 ©, MPIO Seewiesen | Seite 31

## Voltage supply

All consumers are supplied with 3.3 Volts which is produced by the down converter from the 12.8 Volts from the lithium-ion-accumulator. The minimum input voltage for the down converter is 5 Volts.

## Electrical energy storage

The main power supply is ensured by the lithium-ion-accumulator. If the accumulator is removed a capacitor can supply the Animal Presence RFID Data Logger for around 30 seconds.

### 3.3.1 Accumulator

If the whole capacity of a lithium-ionaccumulator is completely used it can have negative effects on the lifetime of the accumulator. Therefore, a certain percentage is not used. The accumulator of the Animal Presence RFID Data Logger uses 83% of the total capacity.

The lithium-ion-accumulator has its own board which is able to communicate with the Animal Presence RFID Data Reader via a data bus.

### 3.3.2 Capacitor

If the energy supply from the accumulator is no longer available, a capacitor with

### 0.22 farad supplies the Animal Presence RFID Data Logger for around 30 sec-

onds. During the discharge, the voltage declines from 3.6 Volts to 1.8 Volts. 1.8 Volts is the minimum working Voltage for the MCU.

### 3.3.3 Conversion loss

The accumulator provides electrical energy with a voltage of 12.8 Volts. The EFM32G230 and other consumers require a significantly smaller voltage of around 3.3 Volts. This reduction of voltage is achieved by a down converter which

voltage | 12.8 V
Nominal capacity | 7.5 Ah
Total capacity | 8.97 Ah
stored energy | 96 Wh

Energy supply

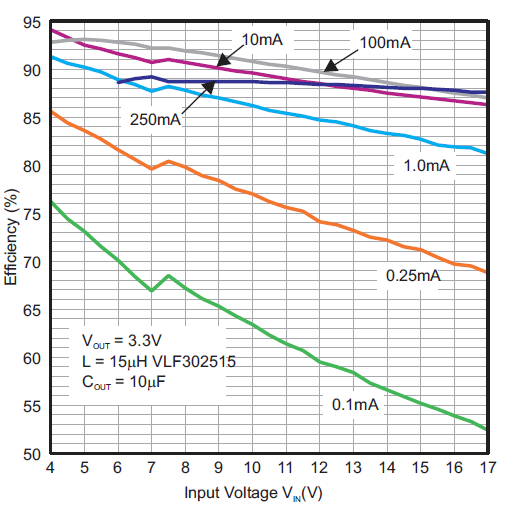
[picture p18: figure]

28.01.2016 | https://www.orn.mpg.de | Copyright 2016 ©, MPIO Seewiesen | Seite 32

is described in chapter 1.2.10. The down converter doesn’t work with transformers but with resistors.

### 3.3.4 Range estimation of the accumulator

Range at maximum power (If the Animal Presence RFID Data Logger is always active and there is no maintenance; connected ra-dio clock but inactive, controller, LED con-nected but off, capacitor, without LCD, SD card, down converter, light barrier, RFID on) | 96 Wh / 0.162 W = 592 hours = 24.66 days
Range at minimum power (If the Animal Presence RFID Data Logger is always inac-tive and there is no maintenance; radio clock, only MCU and light barrier are on) | 96 Wh / 0.0058 W = 16552 hours = 690 days = 1.889 years

The value for the range at minimum power can only theoretically be achieved. In reality the self-discharge causes the accumulator to be discharged earlier.

Operation of the Smart Nest Box

28.01.2016 | https://www.orn.mpg.de | Copyright 2016 ©, MPIO Seewiesen | Seite 33

## Operation of the Smart Nest Box

The operation of the Animal Presence RFID Data Logger with the Smart Nest Box application will be explained in this chapter. This includes the information detailing accumulator replacement, SD card change, software updates, the loading of the accumulator and troubleshooting.

## Accumulator replacement

The accumulator has to be replaced in periodic intervals. The range of an accumulator depends on several factors, including ambient temperature, activity of the Smart Nest Box and energy demand of the Smart Nest Box. The activity of the Smart Nest Box is adapted to vary, depending on the season of the year; as the birds have a higher level of activity during the breeding season. Therefore, the SNB is often in the Active mode and needs more energy. During the wintertime the activity level of the birds is lower and thus the energy demand for the SNB is also lower.

### 4.1.1 Reason for accumulator replacement

The accumulators have boards with three LED’s which indicate the state of charge. If three LED’s are blinking this shows that the accumulator is almost empty. When two LED’s are blinking the accumulator is half full and one LED blinking indicates an almost full accumulator. If there are no LED’s blinking the accumulator is no longer able to supply energy.

When all LED’s are lit permanently this indicates a defect at the accumulator or at the accumulator board. In this case the whole accumulator needs to be changed.

### 4.1.2 Placement of the accumulator

The wind, rain, snow and mist in Europe primarily come from the west. This can be seen visibly on trees where the western-facing sides are often moss-covered. Therefore, placement of the accumulator on the eastern side can minimize the possibility of damage due to oxidation.

Moreover, the accumulator can be placed in a way that water can drain away at an edge, the connector is not on top and the water can flow off from the connector.

Operation of the Smart Nest Box

28.01.2016 | https://www.orn.mpg.de | Copyright 2016 ©, MPIO Seewiesen | Seite 34

If the accumulator becomes over heated it is possible that the accumulator may be damaged. The operating temperature range of the accumulator is between minus 30°C and 55°C according to manufacturer specifications. When the sun shines directly on the accumulator it is possible to exceed this range. Therefore, the accumulator should be protected against direct sunlight through placement on the north-facing side the tree or by shading it in another way.

When placing the accumulator, one should be aware of these external environmental influences and place the accumulator appropriately, because of the high costs of the accumulators.

## SD card change

The SD cards have a large memory size so that the memory may be filled only after several months or even years.

As continuous recording of data is desired and as unexpected malfunctions are always a possibility the time between SD card changes should be as small as possible, so that malfunctions may be detected early through the gathered data. Ideally SD cards should be changed every two or three weeks. Through the gathered data, recording gaps or absurd data can be detected and analysed, then the faulty hardware may be repaired.

## Software update

There are three possible methods to write software code on to the flash memory. The debug probe method from IAR systems and the debug interface method without debug probe are always possible. If software has already been written on the flash memory by either of these methods, an additional method using SD cards is also available.

The microcontroller EFM32G230 contains a flash memory with a memory size of 128 KB. This memory contains the software by which the microprocessor works. 128 KB of memory is a sufficient size for operation, even with very complicated applications such as the Animal Presence RFID Data Logger.

The update options are described in chapter 5.8.

Operation of the Smart Nest Box

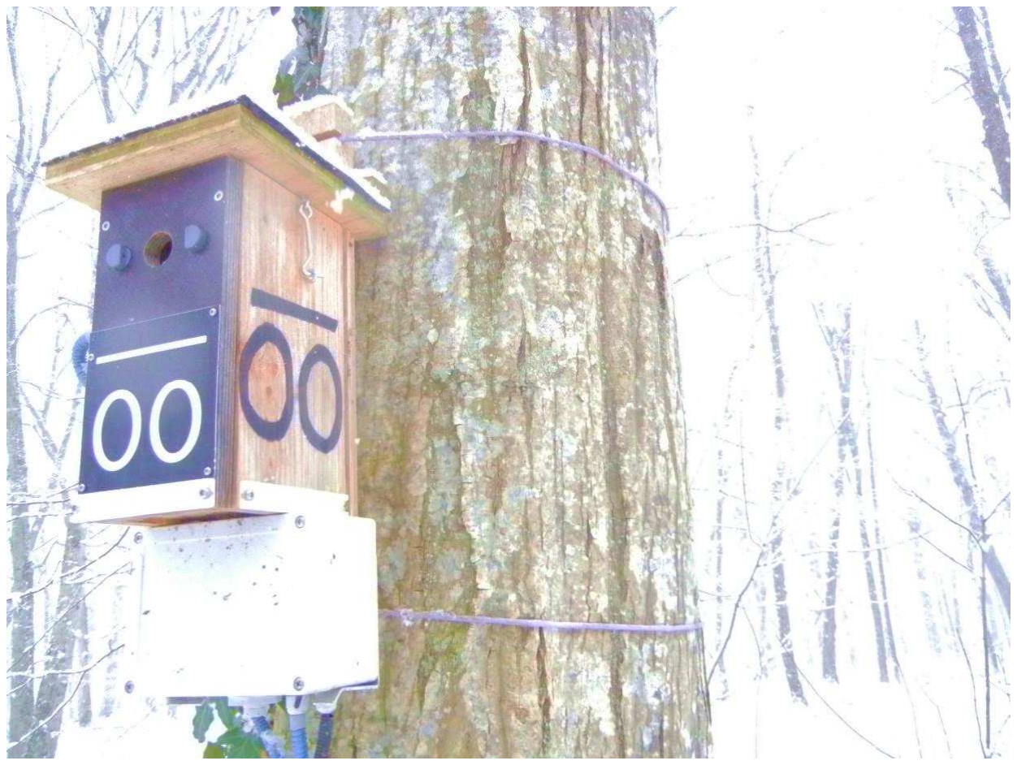
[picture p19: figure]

28.01.2016 | https://www.orn.mpg.de | Copyright 2016 ©, MPIO Seewiesen | Seite 35

## Placement of the accumulator

The Smart Nest Boxes are fastened to trees in a height of around 1,8 meters.

### 4.4.1 Mounting options

The Smart Nest Box is fastened with ropes or tapes which don’t damage the tree. The SNB should be fixed in a way to the tree so that movement due to wind is not possible.

## Loading the accumulator

The accumulators should be changed and charged in regular intervals. The accumulator has to be visually checked for damage when it is changed.

Operation of the Smart Nest Box

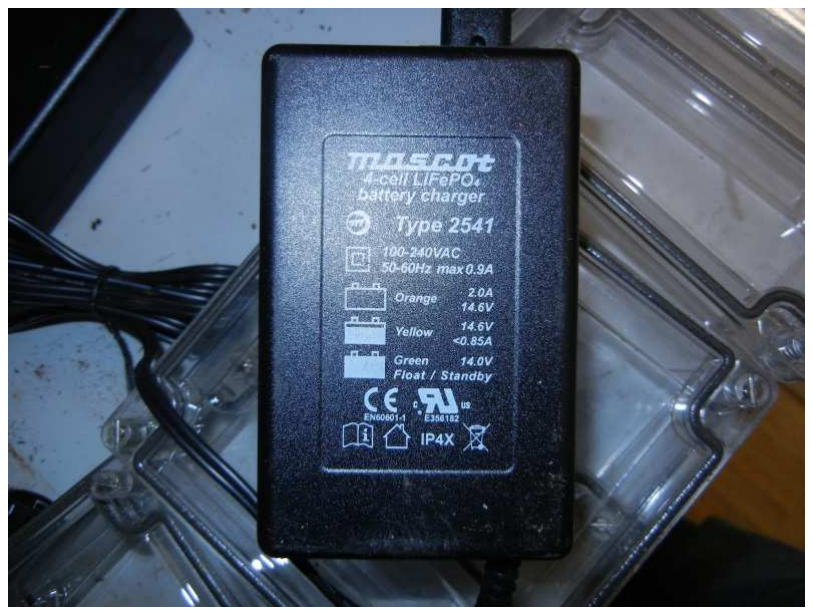
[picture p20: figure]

28.01.2016 | https://www.orn.mpg.de | Copyright 2016 ©, MPIO Seewiesen | Seite 36

### 4.5.1 Recharger

Device description | Mascot type 2541 Li, 4 cell, 2A, Lithium Ion Battery Charger, 35W
Manufacturer | Mascot http://www.mascot.no/home/
Nominal power | 35 W
Battery voltage | 12V
Charging current | Up to 2 A
Recommended battery capacity | 1 – 10 Ah
Loadable cells | 4
Charging characteristic | IUoU

The charge process is separated in to three sections.

### 1. Charging current is 2 A until the voltage reaches 14.7 V 2. Voltage will be held at 14.7 V; Current declines slowly 3. A yellow display shows that the charging current is declined under 1 A

4. If the charging current is below 250 mA the recharger switches off.

### 5. In the maintenance charging module the accumulator voltage will be kept at

13.7 V.

Operation of the Smart Nest Box

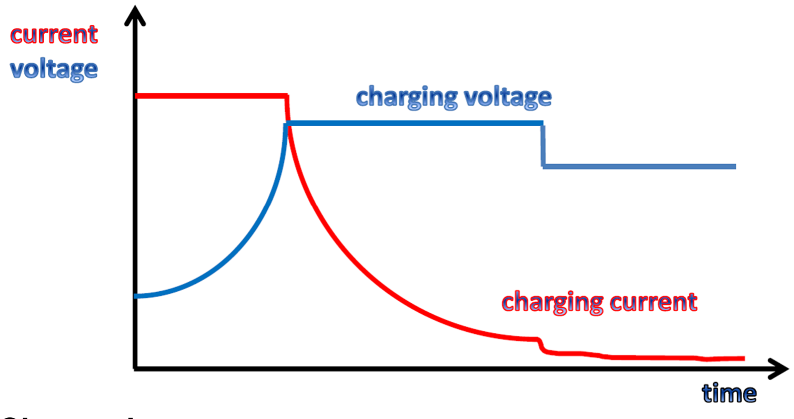
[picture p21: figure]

28.01.2016 | https://www.orn.mpg.de | Copyright 2016 ©, MPIO Seewiesen | Seite 37

### 4.5.2 Charging method IUoU

UIoU means that the initial charging current is constant similar to the CCCV charging method until the final charging voltage is reached. Then the voltage is held at the charging end voltage. This constant high voltage can be harmful for the accumulator and reduce the capacity. Therefore, the voltage will be reduced after a certain amount of time; with that the maintenance charging is initiated. With the reduced voltage the accumulator can be charged permanently and the amount of current is roughly like the self-discharge. The “I” in IUoU stands for constant current, “Uo” stands for constant voltage with charging end voltage and “U” for reduced constant Voltage.

### 4.5.3 Charge time

The accumulators can be charged in roughly one day to ensure that the accumulators are securely fully-loaded.

### 7.5 Ah / 2A = 3.75 h

The charge time is approximately 3.75 hours when the accumulator is totally discharged.

## Troubleshooting at the SNB

The current version of the Smart Nest Box has taken five years of development. Some malfunctions could be encountered and thus lead to experience in troubleshooting and development of specific procedures for malfunctions which may be detected.

Operation of the Smart Nest Box

28.01.2016 | https://www.orn.mpg.de | Copyright 2016 ©, MPIO Seewiesen | Seite 38

### 4.6.1 Troubleshooting in the field

The field troubleshooting takes place after a malfunction is detected through information from the data collected in the SD cards. Incorrect data indicates a malfunction at the SNB.

In older versions of the SNB which have no buttons and no LC display the status of time, date, accumulator status and RFID status were read out through a mobile card reader handheld device. In current versions of the Smart Nest Box the troubleshooting occurs through the three buttons described in chapter 5.7 as well as the LC display described in chapter 1.2.5.

- Button 1 displays the accumulator voltage, remaining accumulator capacity

in mAh and time
- Button 2 displays the date, time and last received transponder code.
- Button 3 can restart the entire system
- The connecting cables from the housing of the mainboard to the front panel

of the Smart Nest box, as well as to the housing of the accumulator must be checked for visible damages.
- If the cause of the failure can’t be found directly the normal procedure is to

replace suspected faulty devices and then check whether the SNB is working correctly.
- Thermal damage as well as damage due to oxidation can be seen easily at

the boards.
- If the failure is not found after replacing the devices it is common to analyse

the affected SNB in the laboratory.

### 4.6.2 Troubleshooting in the laboratory

Via the LEUART-interface the Smart Nest Box can be connected to a PC. This makes it possible to transfer information transmitted by the MCU. This allows for a detailed view into the Smart Nest Box.

If the failure can’t still be found it is recommended to electronically test the hardware to find the malfunction and avoid it in future Smart Nest Box versions.

Software

28.01.2016 | https://www.orn.mpg.de | Copyright 2016 ©, MPIO Seewiesen | Seite 39

## Software

The Software on the flash memory in the Animal Presence RFID Data Logger is programmed with the programming language C. The software is diverse for different versions of the Animal Presence RFID Data Logger. The software needs to be smaller than 128 KB for the flash memory. The software for the Animal Presence RFID Data Logger with the Smart Nest Box application will be described in this chapter. It includes reset options, the reset process, how data is stored and what occurs when the SD card is changed. Also described is how regular queries are stored, what the buttons do and what possible software updates are available exist.

## Reset

The reset can be used to restart the system of the Animal Presence RFID Data Logger when a failure occurs. The procedure for a reset is always the same. The reset is a new start and can be compared with the start of a PC.

### 5.1.1 Possibilities to perform a manual reset

The Animal Presence RFID Data Logger can be restarted manually in two ways:

- Via pushbutton
- Restart after total power loss

### 5.1.2 Procedure after reset

After a reset the following procedure takes place:

### 1. Both LED’s (red and orange) will be illuminated to show that the hardware or

software is active and the LED’s are working.

### 2. The hardware version number and the date are displayed for 4 seconds. Af-

terwards the LED’s are deactivated.

Software

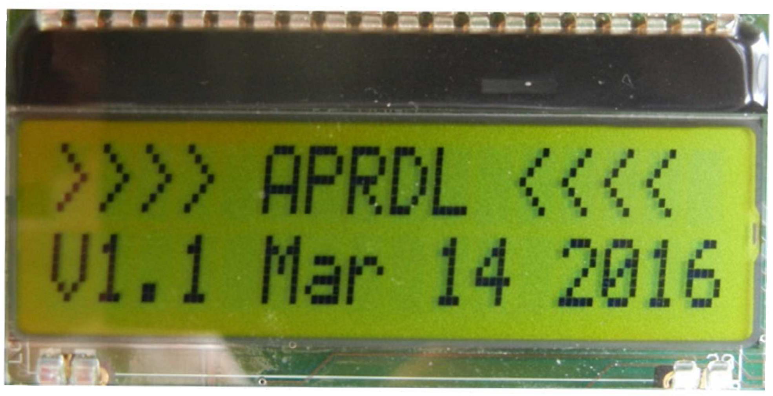
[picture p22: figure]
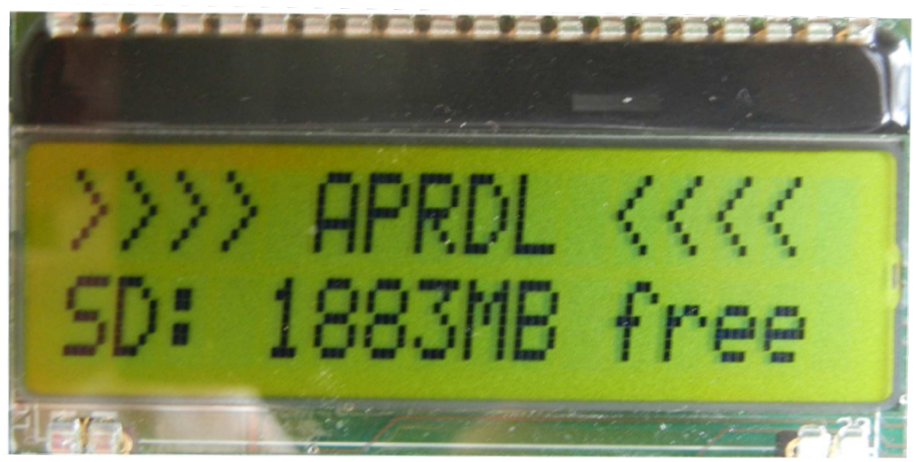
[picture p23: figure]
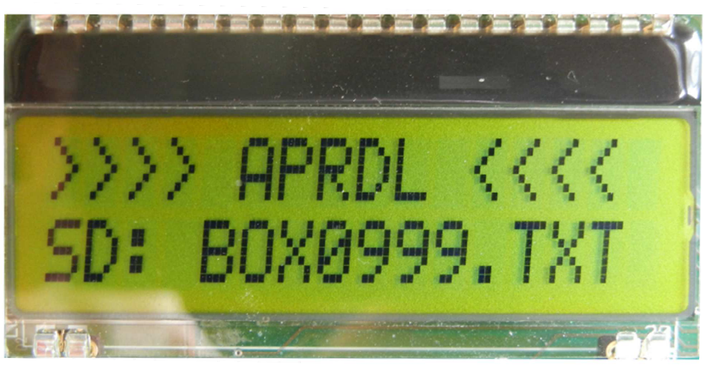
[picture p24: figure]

28.01.2016 | https://www.orn.mpg.de | Copyright 2016 ©, MPIO Seewiesen | Seite 40

### 3. In the case that a SD card is detected the data system will be mounted and the

free space on the SD card will be displayed. The same procedure occurs whenever a SD card is inserted.

### 4. Afterwards it will be searched for a log file with the name “BOXnnnn.TXT”

(nnnn is a random decimal number). In the case that the file exists on the SD card the name will be displayed on the LC display otherwise the file “BOX0999.TXT” will be created.

The radio clock will then be activated to update the date and time. The red LED now flashes to the rhythm of the transmitted data.

Software

28.01.2016 | https://www.orn.mpg.de | Copyright 2016 ©, MPIO Seewiesen | Seite 41

### 5. After the date and time are updated, this information is displayed on the LC

display for 30 seconds. Then the display is switched off and the red LED switched off as well.

### 5.1.3 Reset protocol

If a start or a reset of the Animal Presence RFID Data Logger is carried out some protocol lines are written on the SD card to comprehend the process of the maintenance.

00000000-000000 APRDL V1.1 (Mar 14 2016 14:41:54)

20140101-120004 DCF77: Enabled

20140101-120004 SD-Card Inserted

20140101-120004 SD-Card Initialized

20140101-120004 SD-Card File System mounted

20140101-120004 SD-Card 1883MB free

20140101-120004 Using Filename BOX0999.TXT

20140101-120004 MCU: EFM32G230F128 HW-ID: 0x241E6D0354224957

20140101-120004 Battery Manufacturer Name : | Dynamis
20140101-120004 Battery Manufacturer Data : | 61.90002/15790
20140101-120004 Battery Device Name | : | BMS2-4_V1.0
20140101-120004 Battery Device Type | : | Lithium-Ion
20140101-120004 Battery Serial Number | : 00008
20140101-120004 Battery Design Voltage | : 3.300V per cell
20140101-120004 Battery Design Capacity | : 7500mAh

20140101-120004 Battery Full Charge Capac.: 7500mAh

20140101-120004 Battery Remaining Capacity: 4306mAh

20140101-120005 Battery Runtime to empty | : More than 6 weeks
20140101-120005 Battery Actual Voltage | : 13.1V
20140101-120005 Battery Actual Current | : | 3mA

Software

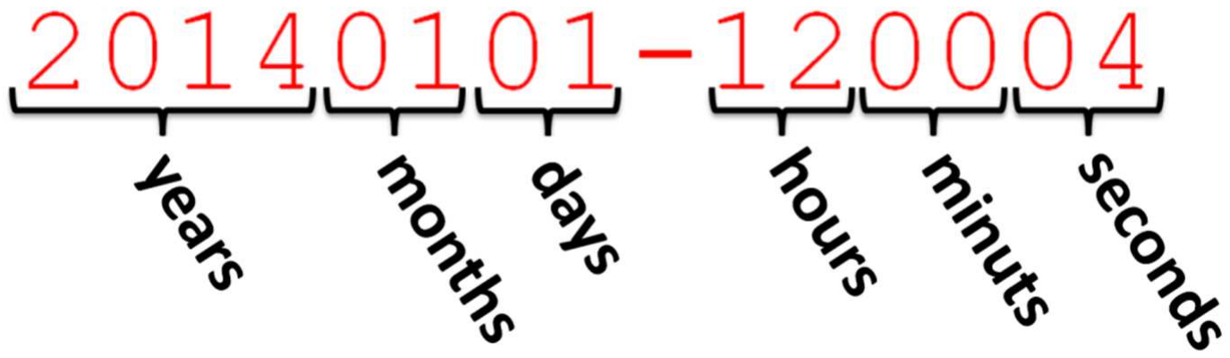
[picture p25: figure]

28.01.2016 | https://www.orn.mpg.de | Copyright 2016 ©, MPIO Seewiesen | Seite 42

## Data storage

All important information from the RAM memory will be saved in a txt-file on the SD card.

Every event or stored message begins with the date and time of the event.

Following the date and time will be the actual status message.

## Procedure after SD card change

After a new SD card is plugged in the following procedure starts.

1. It displays that a new SD card has been detected.

20140101-120004 SD-Card Inserted

20140101-120004 SD-Card Initialized

20140101-120004 SD-Card File System mounted

2. The following line shows how much free space remains on the SD card.

20140101-120011 SD-Card 1880MB free

### 3. Afterwards it will search for a log file with the name „BOXnnnn.TXT“ (nnnn is a

random decimal number). In case that the file exists on the SD card the name will be displayed on the LC display otherwise the file „BOX0999.TXT“ will be created.

20140101-120011 Using Filename BOX0999.TXT

20140101-120011 Media Change: BOX0999.TXT -> BOX0020.TXT

Software

28.01.2016 | https://www.orn.mpg.de | Copyright 2016 ©, MPIO Seewiesen | Seite 43

### 4. The hardware ID will be displayed, which is a unique number allocated to each

Animal Presence RFID Data Logger, so they can be identified individually.

20140101-120011 MCU: EFM32G230F128 HW-ID: 0x24B4010253FD82EE

### 5. The status of the accumulator is then displayed, including the manufacturer

name, manufacturer data, device name, device type, serial number, design voltage, design capacity, total capacity, remaining capacity, remaining time at actual current and at least the measured actual voltage.

20140101-120011 Battery Manufacturer Name : | Dynamis
20140101-120011 Battery Manufacturer Data : | 61.90002/15790
20140101-120011 Battery Device Name | : | BMS2-4_V0.3
20140101-120011 Battery Device Type | : | Lithium-Ion
20140101-120011 Battery Serial Number | : 00008
20140101-120011 Battery Design Voltage | : 3.300V per cell
20140101-120012 Battery Design Capacity | : 7500mAh

20140101-120012 Battery Full Charge Capac.: 8968mAh

20140101-120012 Battery Remaining Capacity: 4122mAh

20140101-120012 Battery Runtime to empty | : More than 6 weeks
20140101-120012 Battery Actual Voltage | : 13.149V
20140101-120012 Battery Actual Current | : | 3mA

### 6. The time of the microcontroller is updated through the signals from the radio

clock. This process usually only takes a few minutes.

20140101-120856 DCF77: Time Frame 1 is 20160315-143100

20140101-120956 DCF77: Time Frame 2 is 20160315-143200

20160315-143200 Initial Time Synchronisation

20160315-143200 DCF77: Time Synchronization 14:32:00

20160315-143200 DCF77: Disabled

Software

28.01.2016 | https://www.orn.mpg.de | Copyright 2016 ©, MPIO Seewiesen | Seite 44

## Periodic routine queries

### 5.4.1 Time update

Every 24 hours, during the night the time from the MCU is updated by the signals from the radio clock.

20160319-015500 DCF77: Enabled

20160319-015701 DCF77: Time Frame 1 is 20160319-015700

20160319-015801 DCF77: Time Frame 2 is 20160319-015800

20160319-015800 DCF77: Time Synchronization 01:58:00

20160319-015800 DCF77: Disabled

If the radio clock is not available, no update occurs and there will be no synchronization message.

### 5.4.2 Battery status query

In regular intervals the status of the accumulator is written into the RAM memory and on the SD card. In addition to this message the actual current is displayed. The remaining runtime of the accumulator is calculated from data from the accumulator board. The remaining capacity and the actual current are used for this calculation.

20160316-120000 Battery Remaining Capacity: 4337mAh

20160316-120000 Battery Runtime to empty | : More than 6 weeks
20160316-120000 Battery Actual Voltage | : 13.1V
20160316-120000 Battery Actual Current | : | 1mA

## Recorded events

The main task of the Animal Presence RFID Data Logger is to record the behaviour of animals. In the Smart Nest Box application this is made through the recordings from the light barrier activity and transponder detections.

Software

28.01.2016 | https://www.orn.mpg.de | Copyright 2016 ©, MPIO Seewiesen | Seite 45

### 5.5.1 Light barrier activity

The light barriers are always active and are always supplied with electrical energy. They are the trigger for the RFID Reader which is by far the largest energy consumer.

20160323-112408 LBO:ON | # Light barrier outer on
20160323-112408 LBI:ON | # Light barrier inner on
20160323-112408 LBO:off | # Light barrier outer off
20160323-112408 LBI:off | # Light barrier inner off

### 5.5.2 Transponder activity

The RFID reader is switched on by light barrier activity. This needs to occur very quickly as the transponder may be rapidly moving through the barrier and its numberneeds to be read completely. Particularly for transponders in birds, it needs to be to read out entirely during the flight into the nest box through the entrance hole with the RFID reader. The birds have a high velocity while entering in the nest box. However, their velocity when leaving the nest box is not as fast.

20150723-154010 RFID is powered ON

20150723-154010 Transponder: D5CD24B43A6F0001

20150723-154122 RFID is powered off

Because it is likely to detect further activity after a transponder is detected, the RFID remains on for an additional 6 minutes after the last transponder signal

### 5.5.3 Standard recording

In the following lines there are typical status messages from the Animal Presence RFID Data Logger with the Smart Nest Box application. It is an exemplary record from an incoming bird which is remaining in the box for more than 6 minutes.

LBO:ON | # Light barrier outer on
RFID is powered ON | # RFID active
Transponder: D5CD24B43A6F0001 | # Transponder reading
LBI:ON | # Light barrier inner on
LBO:off | # Light barrier outer off

Software

28.01.2016 | https://www.orn.mpg.de | Copyright 2016 ©, MPIO Seewiesen | Seite 46
LBI:off | # Light barrier inner off
RFID is powered off | # RFID inactive

By using two light barriers, the direction of the flight path can be detected. In the example above a subject is flying initially through the outer and then through the inner light barrier. This shows that the subject has flown into the nest box.

## Occurrences when it is not possible to write on the SD card

When the SD card is full or if there is no SD card is in SD card slot an error message is written on the LEUART-BUS. This message is not written on the SD card and can only be seen on the LEUART-BUS. It is not common that data is lost due to the absence of an SD card, and the internal memory is full because the 2 KB of provided memory is enough for many messages to be stored.

## Expiry after keystroke

The Animal Presence RFID Data Logger has three buttons to display messages on the LC display or to restart the system. The buttons are explained in chapter 1.2.7 and the installation site can be seen in chapter 1.2.2.

### 5.7.1 Display the light barrier status and the accumulator status

with button S1

After pressing the S1 button the current
status of the two light barriers (LBO = Light Barrier Outer, LBI = Light Barrier Inner, "XX" = active, "" = inactive) are displayed on the LC display. The status of the accumulator is also displayed through current voltage and remaining capacity in mAh.

Software

28.01.2016 | https://www.orn.mpg.de | Copyright 2016 ©, MPIO Seewiesen | Seite 47

### 5.7.2 Display the date, time and the last received transponder

number with button S2

After pressing the S2 button the current date and time as well as the last received transponder number will be displayed on the LC display. When the S2 button is pressed for more than 5 seconds the
last received transponder code will be
deleted. This allows it to test the RFID
reader with the same transponder more than once. If no button is pressed for more than 20 seconds, the LC display will be shut off.

### 5.7.3 Initiating a restart of the system

After pressing the S3 button the whole data system of the Animal Presence RFID Data Logger will be restarted. The procedure of the restart is described in chapter 5.1.2.

## Update options

There are three possibilities to write software code on the flash memory.

The microcontroller EFM32G230 contains a flash memory with 128 KB memory size. This memory contains the software by which the microprocessor has to work. 128 KB memory is sufficient memory space to realize even very complicated applications with the Animal Presence RFID Data Logger.

Software

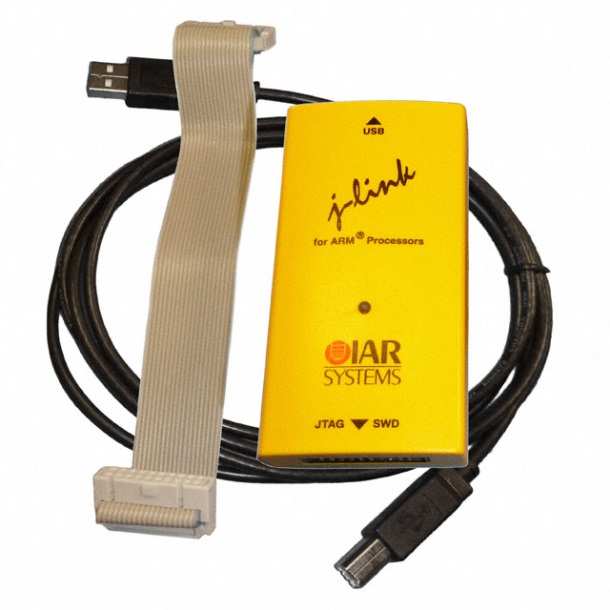
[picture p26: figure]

28.01.2016 | https://www.orn.mpg.de | Copyright 2016 ©, MPIO Seewiesen | Seite 48

### 5.8.1 IAR Systems Debug Probe

Through the debug probe from IAR systems it is possible to load compiled software code on the flash memory. The software from IAR for the debug probe is necessary for this.

IAR Systems also distribute the software IAR Embedded Workbench to create and compile C code. The compiled C code can be loaded on the flash memory by the debug probe.

### 5.8.2 With an USB cable and the 10-pole Interface connector

This method only allows HEX and BIN files to be transferred to the flash memory. The original C code cannot be transmitted without the debug probe.

### 5.8.3 Per SD card and boot loader

If software has already been written on the flash memory by either of the methods from chapter 5.8.1 or 5.8.2 a third method through a boot loader is available. The boot loader searches potential software code on the inserted SD card.

Contact details

28.01.2016 | https://www.orn.mpg.de | Copyright 2016 ©, MPIO Seewiesen | Seite 49

## Contact details

address | Max-Planck-Institute for Ornithology Eberhard-Gwinner-Str. 82319 Seewiesen
web address | http://www.orn.mpg.de/
electronics developer | Dipl. Ing. (FH) Peter Loës
e-mail address | loes@orn.mpg.de
telephone number | Tel: +49 8157 932-330

Links to the datasheets

28.01.2016 | https://www.orn.mpg.de | Copyright 2016 ©, MPIO Seewiesen | Seite 50

## Links to the datasheets

EFM32G230

IAR J Tag ARM

LC display

SD memory card connector

Button

Capacitor

Jack connector

USB cable

Down converter

LED’S

Radio clock

Light barrier

RFID reader

RFID-transponder

Housing for the main board

Housing for the accumulator

Battery charger Fronius

Battery charger Mascot

Battery cell

Inhaltsverzeichnis

28.01.2016 | https://www.orn.mpg.de | Copyright 2016 ©, MPIO Seewiesen | Seite 51

## Table of contents

List of abbreviations | 3
System Overview | 4
General Description of Functions | 4
System configuration main circuit board | 6

### 1.2.1 Block diagram | 6

### 1.2.2 Hardware Illustration | 7

### 1.2.3 EFM32 microcontroller | 8

### 1.2.4 Debug Interface (DBG) | 9

### 1.2.5 Liquid Crystal Display (LCD) | 9

### 1.2.6 SD Memory Card Connector | 10

### 1.2.7 Buttons | 10

### 1.2.8 Capacitor | 10

### 1.2.9 Jack connector as interface to a PC | 11

### 1.2.10 Down converter | 11

### 1.2.11 LED’s | 12

### 1.2.12 Connector for the peripherals | 12

System configuration secondary board with radio clock | 12

### 1.3.1 Block diagram | 13

### 1.3.2 Hardware Illustration | 13

### 1.3.3 Radio clock DCF (77,5KHz) | 14

Peripheral equipment Smart Nest Box | 15

### 1.4.1 Block diagram Smart Nest Box front panel | 15

Inhaltsverzeichnis

28.01.2016 | https://www.orn.mpg.de | Copyright 2016 ©, MPIO Seewiesen | Seite 52

### 1.4.2 Hardware illustration | 16

### 1.4.3 Light barrier | 17

### 1.4.4 RFID | 17

Accumulator | 20
Pin assignment and connectors | 21

### 1.6.1 Pins for debugging | 21

### 1.6.2 Pin assignment | 21

Housing | 23

### 1.7.1 Housing for the main board | 23

### 1.7.2 Housing for the accumulator | 24

General working conditions | 25
Energy supply | 26
Current supply | 26

### 3.1.1 ARM Cortex Processor | 26

### 3.1.2 RFID reader | 27

### 3.1.3 Light barrier | 27

### 3.1.4 LC display | 27

### 3.1.5 Radio Clock | 27

### 3.1.6 LED | 27

### 3.1.7 Accumulator LED’s and self-discharge | 28

### 3.1.8 Overview of the nominal currents | 28

### 3.1.9 Overview of the currents in the different operating modes | 29

Voltage supply | 31

Inhaltsverzeichnis

28.01.2016 | https://www.orn.mpg.de | Copyright 2016 ©, MPIO Seewiesen | Seite 53
Electrical energy storage | 31

### 3.3.1 Accumulator | 31

### 3.3.2 Capacitor | 31

### 3.3.3 Conversion loss | 31

### 3.3.4 Range estimation of the accumulator | 32

Operation of the Smart Nest Box | 33
Accumulator replacement | 33

### 4.1.1 Reason for accumulator replacement | 33

### 4.1.2 Placement of the accumulator | 33

SD card change | 34
Software update | 34
Placement of the accumulator | 35

### 4.4.1 Mounting options | 35

Loading the accumulator | 35

### 4.5.1 Recharger | 36

### 4.5.2 Charging method IUoU | 37

### 4.5.3 Charge time | 37

Troubleshooting at the SNB | 37

### 4.6.1 Troubleshooting in the field | 38

### 4.6.2 Troubleshooting in the laboratory | 38

Software | 39
Reset | 39

### 5.1.1 Possibilities to perform a manual reset | 39

Inhaltsverzeichnis

28.01.2016 | https://www.orn.mpg.de | Copyright 2016 ©, MPIO Seewiesen | Seite 54

### 5.1.2 Procedure after reset | 39

### 5.1.3 Reset protocol | 41

Data storage | 42
Procedure after SD card change | 42
Periodic routine queries | 44

### 5.4.1 Time update | 44

### 5.4.2 Battery status query | 44

Recorded events | 44

### 5.5.1 Light barrier activity | 45

### 5.5.2 Transponder activity | 45

### 5.5.3 Standard recording | 45

Occurrences when it is not possible to write on the SD card | 46
Expiry after keystroke | 46

### 5.7.1 Display the light barrier status and the accumulator status with button

S1 46

### 5.7.2 Display the date, time and the last received transponder code with

button S2 | 47

### 5.7.3 Initiating a restart of the system | 47

| Update options | 47

### 5.8.1 IAR Systems Debug Probe | 48

### 5.8.2 With an USB cable and the 10-pole Interface connector | 48

### 5.8.3 Per SD card and boot loader | 48

Contact details | 49
Links to the datasheets | 50

Inhaltsverzeichnis

28.01.2016 | https://www.orn.mpg.de | Copyright 2016 ©, MPIO Seewiesen | Seite 55
Table of contents | 51

Literaturverzeichnis

28.01.2016 | https://www.orn.mpg.de | Copyright 2016 ©, MPIO Seewiesen | Seite 56

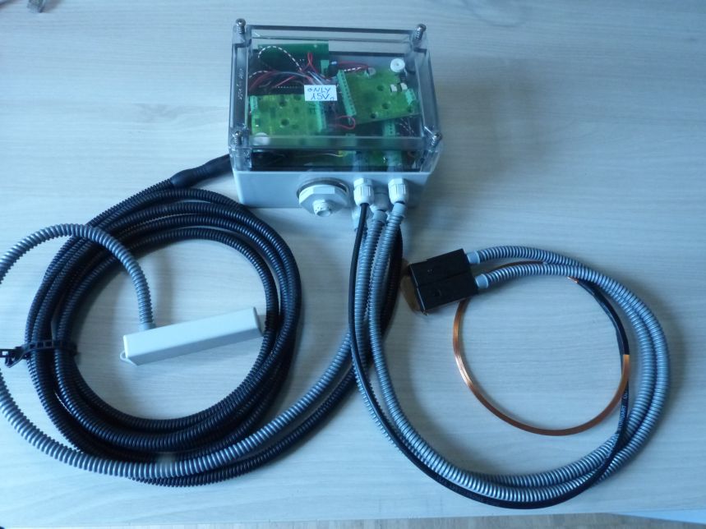
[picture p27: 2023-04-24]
Getting_Started_Tutorial/3_SNB_LR_LB.jpg

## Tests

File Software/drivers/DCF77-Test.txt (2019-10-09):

DCF77 TEST
==========
2016-04-13, rage

Setzen der initialen Zeit auf Winterzeit
----------------------------------------
Die Testuhr wird auf 07:52 MEZ gestellt (2016.02.26), die DCF77
synchronisiert nach zwei Frames auf 07:54

***** APRDL V1.1 *****

00000000-000000 APRDL V1.1 (Apr 13 2016 18:40:43)
20140101-120003 DCF77: Enabled
20140101-120003 SD-Card Inserted
20140101-120205 DCF77: Time Frame 1 is 20160226-075300
20140101-120305 DCF77: Time Frame 2 is 20160226-075400
20160226-075400 Initial Time Synchronisation
20160226-075400 DCF77: Time Synchronization 07:54:00 (MEZ)
20160226-075400 DCF77: Disabled

Setzen der initialen Zeit auf Sommerzeit
----------------------------------------
Die DCF77 wird auf 20:46 MESZ gestellt (2016.04.13), die DCF77
synchronisiert nach zwei Frames auf 20:49

***** APRDL V1.1 *****

00000000-000000 APRDL V1.1 (Apr 13 2016 18:40:43)
20140101-120003 DCF77: Enabled
20140101-120003 SD-Card Inserted
20140101-120227 DCF77: Time Frame 1 is 20160413-204800
20140101-120327 DCF77: Time Frame 2 is 20160413-204900
20160413-204900 Initial Time Synchronisation
20160413-204900 DCF77: Time Synchronization 20:49:00 (MESZ)
20160413-204900 DCF77: Changing time zone from MEZ to MESZ
20160413-204900 DCF77: Disabled

Wechsel von Winter zu Sommerzeit
--------------------------------
Um den Wechsel innerhalb von 10Minuten testen zu können, geschieht dies in 2 Phasen:

Phase 1
1. MEZ auf 01:49 stellen (OHNE das Umschalten von MEZ auf MESZ anzuzeigen)
2. DCF77 synchronisiert auf 01:51 und schaltet sich dann ab
Phase 2
2. Ab 01:53 das Umschalten von MESZ auf MEZ anzeigen (Bit 16, await change)
3. Um 01:55 schaltet sich DCF77 wieder ein um den täglichen Sync. vorzunehmen
4. Um 01:57 (nach zwei Frames) erfolgt die erste Synchronisation
5. Da das "await change" Bit gesetzt ist, schaltet die DCF77 nicht sofort nach dem
   zweiten Frame wieder ab, sondern erst, nachdem MEZ auf MESZ umgestellt wurde,
   d.h. um 03:00

***** APRDL V1.1 *****

00000000-000000 APRDL V1.1 (Apr 13 2016 18:40:43)
20140101-120003 DCF77: Enabled
20140101-120003 SD-Card Inserted
20140101-120210 DCF77: Time Frame 1 is 20160326-015000
20140101-120310 DCF77: Time Frame 2 is 20160326-015100
20160326-015100 Initial Time Synchronisation
20160326-015100 DCF77: Time Synchronization 01:51:00 (MEZ)
20160326-015100 DCF77: Disabled
20160326-015500 DCF77: Enabled
20160326-015702 DCF77: Time Frame 1 is 20160327-015700
20160326-015802 DCF77: Time Frame 2 is 20160327-015800
20160327-015800 DCF77: Time Synchronization 01:58:00 (MEZ)
20160327-015859 DCF77: Time Frame 3 is 20160327-015900
20160327-015900 DCF77: Time Synchronization 01:59:00 (MEZ)
20160327-015959 DCF77: Time Frame 4 is 20160327-030000
20160327-030000 DCF77: Time Synchronization 03:00:00 (MESZ)
20160327-030000 DCF77: Changing time zone from MEZ to MESZ
20160327-030000 DCF77: Disabled

Wechsel von Sommer zu Winterzeit
--------------------------------
Um den Wechsel innerhalb von 10Minuten testen zu können, geschieht dies in 2 Phasen:

Phase 1
1. MESZ auf 02:49 stellen (OHNE das Umschalten von MESZ auf MEZ anzuzeigen)
2. DCF77 synchronisiert auf 02:51 und schaltet sich dann ab
Phase 2
2. Ab 02:53 das Umschalten von MESZ auf MEZ anzeigen (Bit 16, await change)
3. Um 02:55 schaltet sich DCF77 wieder ein um den täglichen Sync. vorzunehmen
4. Um 02:57 (nach zwei Frames) erfolgt die erste Synchronisation
5. Da das "await change" Bit gesetzt ist, schaltet die DCF77 nicht sofort nach dem
   zweiten Frame wieder ab, sondern erst, nachdem MESZ auf MEZ umgestellt wurde,
   d.h. um 02:00

***** APRDL V1.1 *****

00000000-000000 APRDL V1.1 (Apr 13 2016 18:40:43)
20140101-120003 DCF77: Enabled
20140101-120003 SD-Card Inserted
20140101-120145 DCF77: Time Frame 1 is 20161028-025000
20140101-120245 DCF77: Time Frame 2 is 20161028-025100
20161028-025100 Initial Time Synchronisation
20161028-025100 DCF77: Time Synchronization 02:51:00 (MESZ)
20161028-025100 DCF77: Changing time zone from MEZ to MESZ
20161028-025100 DCF77: Disabled
20161028-025500 DCF77: Enabled
20161028-025701 DCF77: Time Frame 1 is 20161030-025700
20161028-025801 DCF77: Time Frame 2 is 20161030-025800
20161030-025800 DCF77: Time Synchronization 02:58:00 (MESZ)
20161030-025859 DCF77: Time Frame 3 is 20161030-025900
20161030-025900 DCF77: Time Synchronization 02:59:00 (MESZ)
20161030-025959 DCF77: Time Frame 4 is 20161030-020000
20161030-020000 DCF77: Time Synchronization 02:00:00 (MEZ)
20161030-020000 DCF77: Changing time zone from MESZ to MEZ
20161030-020000 DCF77: Disabled

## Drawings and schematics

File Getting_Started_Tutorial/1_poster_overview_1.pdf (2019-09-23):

## Animal Presence RFID Data Logger (APRDL)

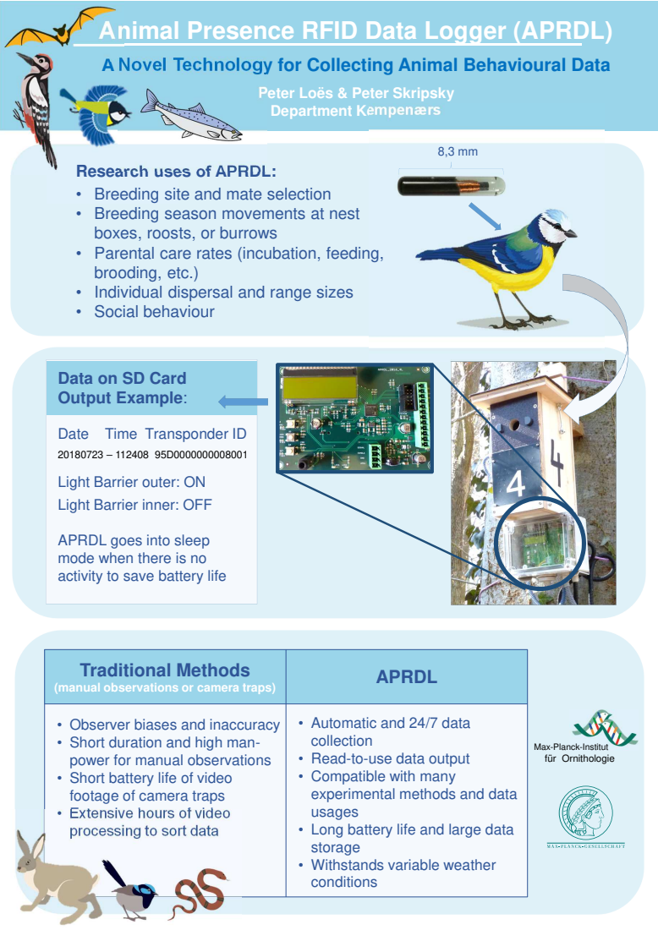
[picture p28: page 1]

A Novel Technology for Collecting Animal Behavioural Data

Peter Loës & Peter Skripsky
Department Kempenærs

Research uses of APRDL:
• Breeding site and mate selection
• Breeding season movements at nest
boxes, roosts, or burrows
• Parental care rates (incubation, feeding,
brooding, etc.)
• Individual dispersal and range sizes
• Social behaviour

Data on SD Card
Output Example:

Date Time Transponder ID

Light Barrier outer: ON
Light Barrier inner: OFF

APRDL goes into sleep
mode when there is no
activity to save battery life

Traditional Methods (manual observations or camera traps) | APRDL

• Observer biases and inaccuracy • Short duration and high man-power for manual observations • Short battery life of video footage of camera traps • Extensive hours of video processing to sort data | • Automatic and 24/7 data collection • Read-to-use data output • Compatible with many experimental methods and data usages • Long battery life and large data storage • Withstands variable weather conditions

Max-Planck-Institut
für Ornithologie

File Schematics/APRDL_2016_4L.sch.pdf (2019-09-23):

# Power Input

# EFM32 Power Regulator

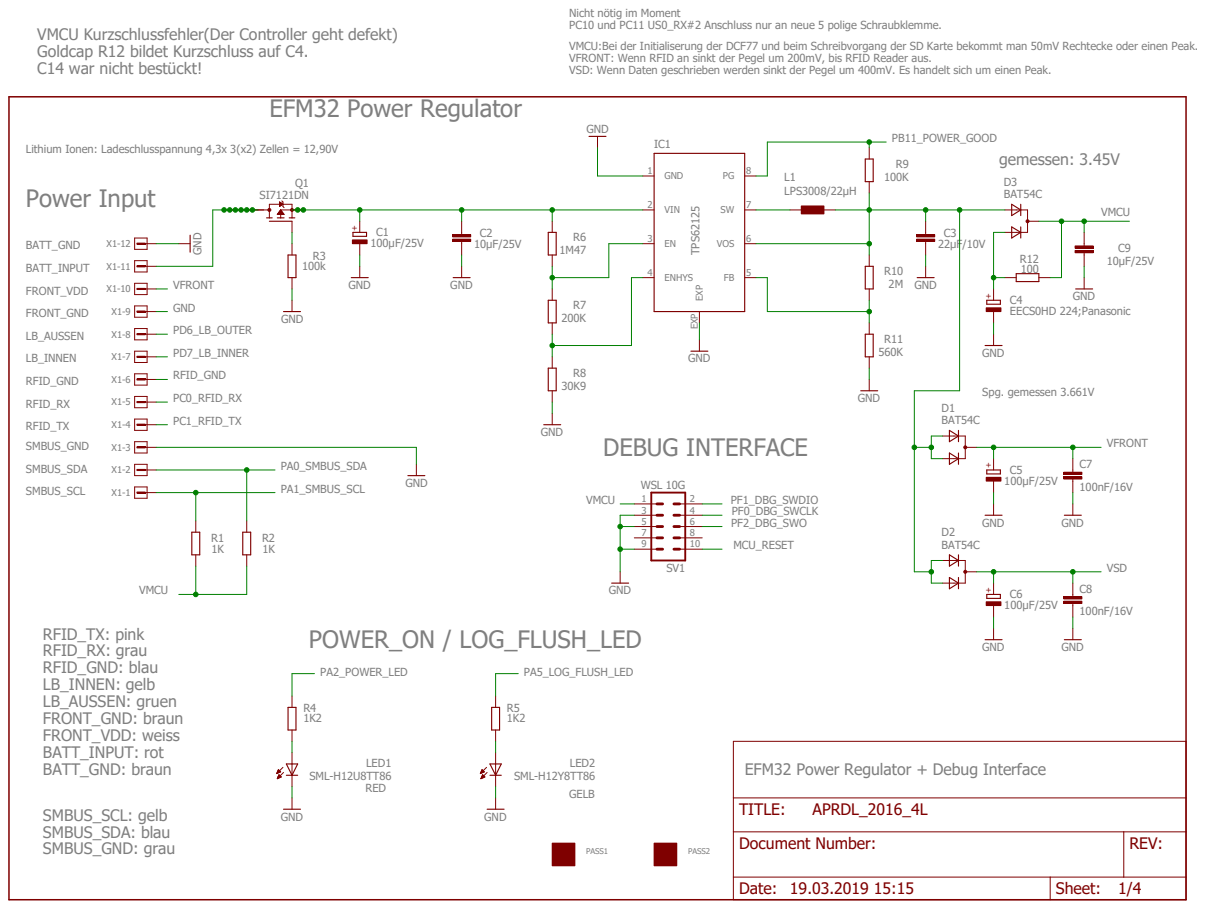
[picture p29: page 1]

Nicht nötig im Moment
PC10 und PC11 US0_RX#2 Anschluss nur an neue 5 polige Schraubklemme.

VMCU Kurzschlussfehler(Der Controller geht defekt)
Goldcap R12 bildet Kurzschluss auf C4.
C14 war nicht bestückt!

VMCU:Bei der Initialiserung der DCF77 und beim Schreibvorgang der SD Karte bekommt man 50mV Rechtecke oder einen Peak.
VFRONT: Wenn RFID an sinkt der Pegel um 200mV, bis RFID Reader aus.
VSD: Wenn Daten geschrieben werden sinkt der Pegel um 400mV. Es handelt sich um einen Peak.

Lithium Ionen: Ladeschlusspannung 4,3x 3(x2) Zellen = 12,90V

EFM32 Power Regulator + Debug Interface

Document Number: | REV:

Date: 19.03.2019 15:15 | Sheet: 1/4

# EFM32 I/O + POWER

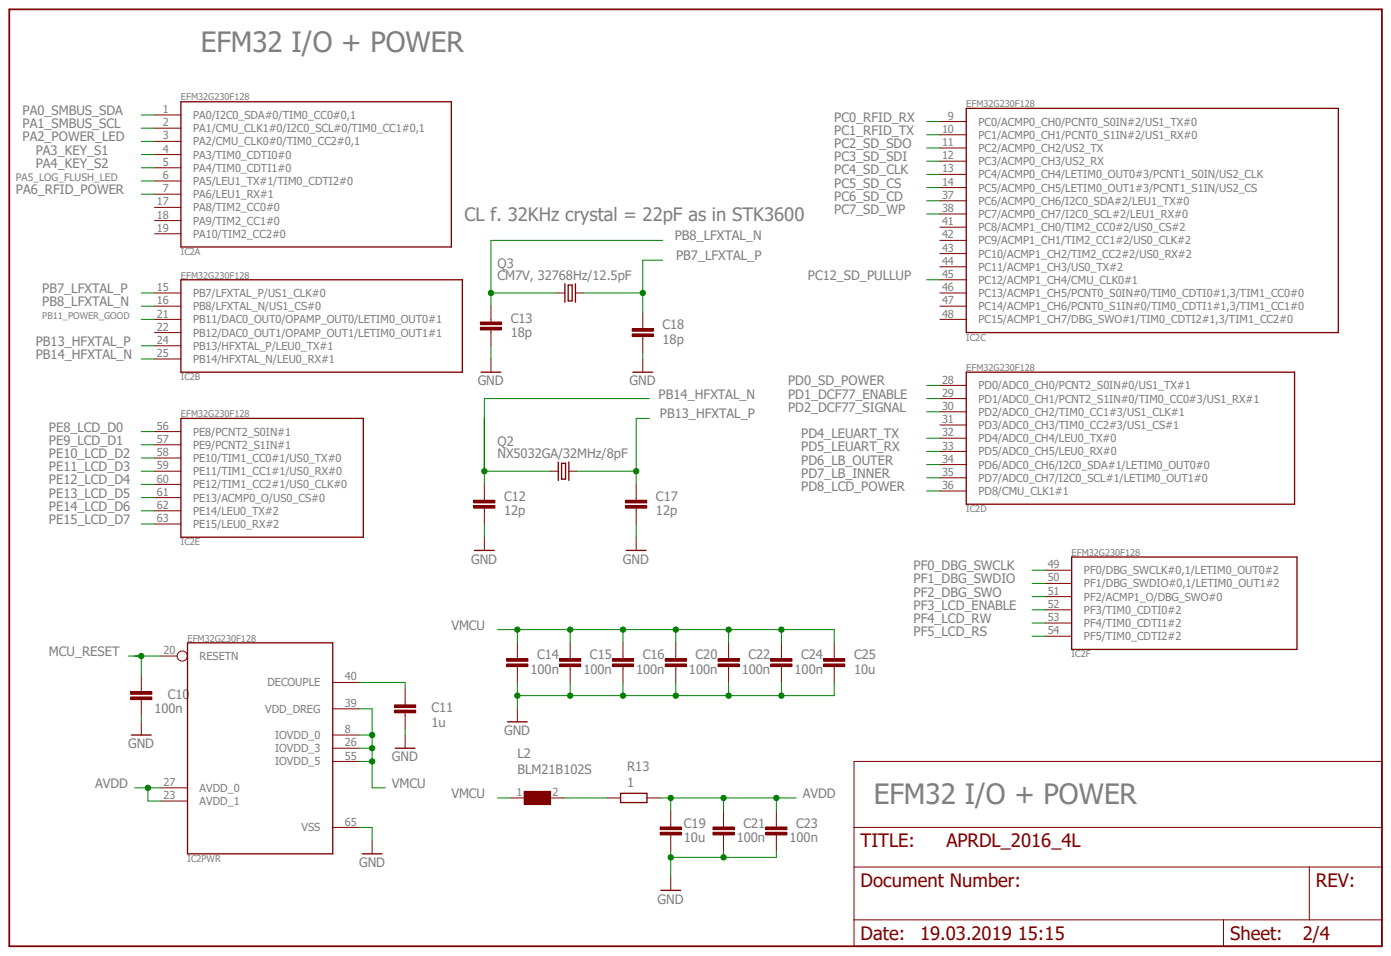
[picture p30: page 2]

CL f. 32KHz crystal = 22pF as in STK3600

Document Number: | REV:

Date: 19.03.2019 15:15 | Sheet: 2/4

## Activity

# SD SOCKET + DCF77 + LEUART+ PUSHBUTTON

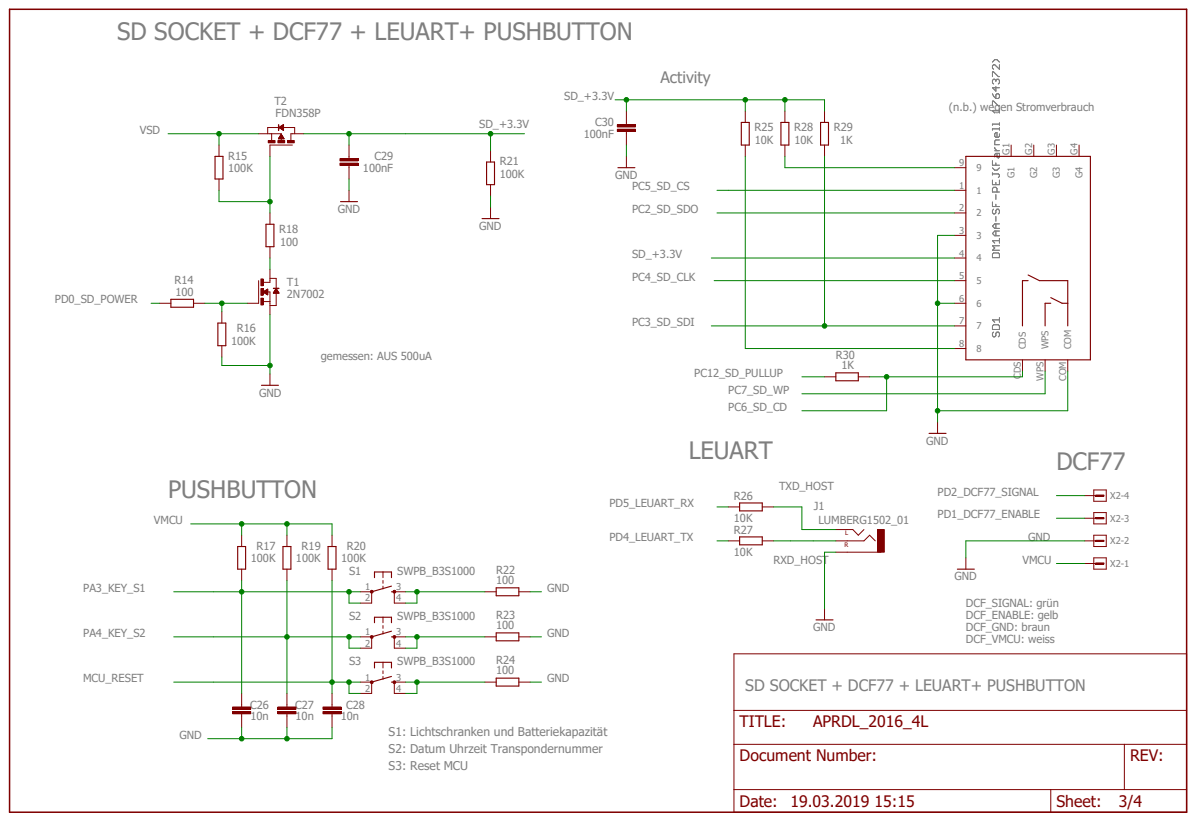
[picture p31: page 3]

SD SOCKET + DCF77 + LEUART+ PUSHBUTTON

Document Number: | REV:

Date: 19.03.2019 15:15 | Sheet: 3/4

# LCD ANZEIGE

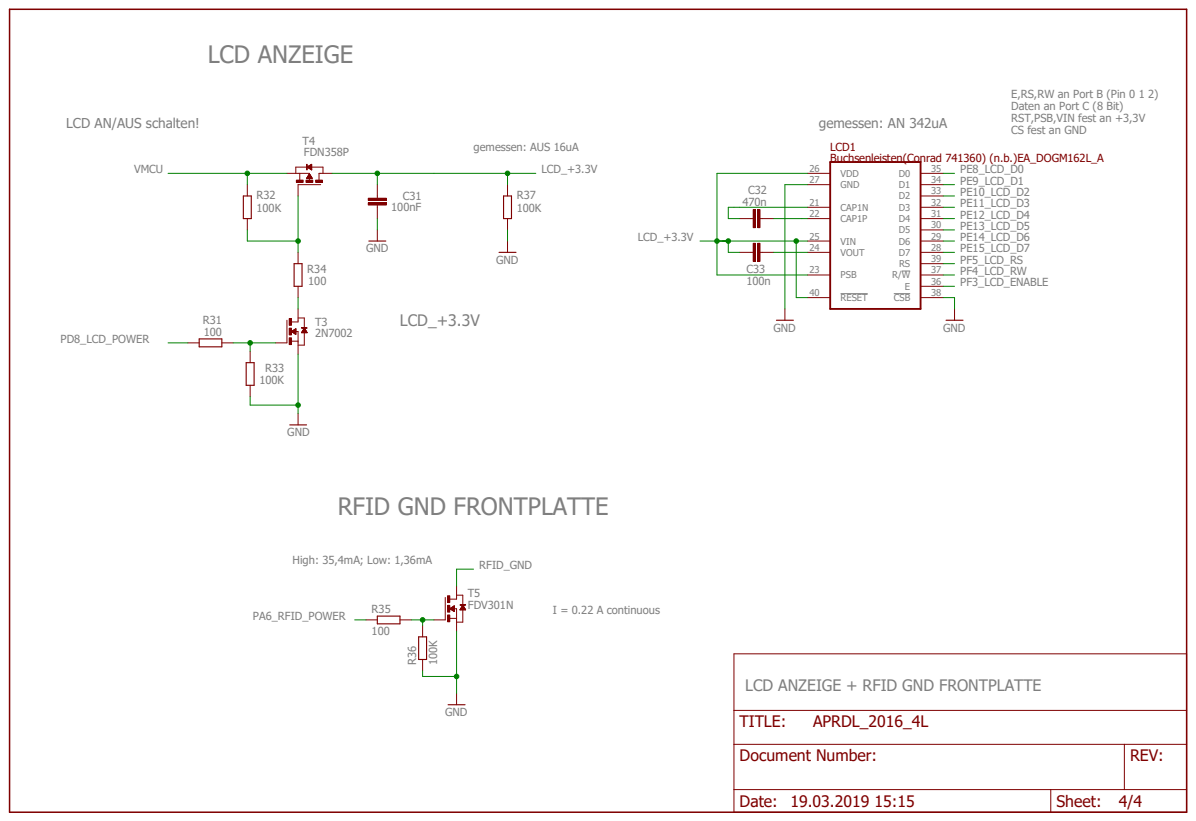
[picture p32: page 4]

E,RS,RW an Port B (Pin 0 1 2)
Daten an Port C (8 Bit)
RST,PSB,VIN fest an +3,3V
CS fest an GND

LCD ANZEIGE + RFID GND FRONTPLATTE

Document Number: | REV:

Date: 19.03.2019 15:15 | Sheet: 4/4

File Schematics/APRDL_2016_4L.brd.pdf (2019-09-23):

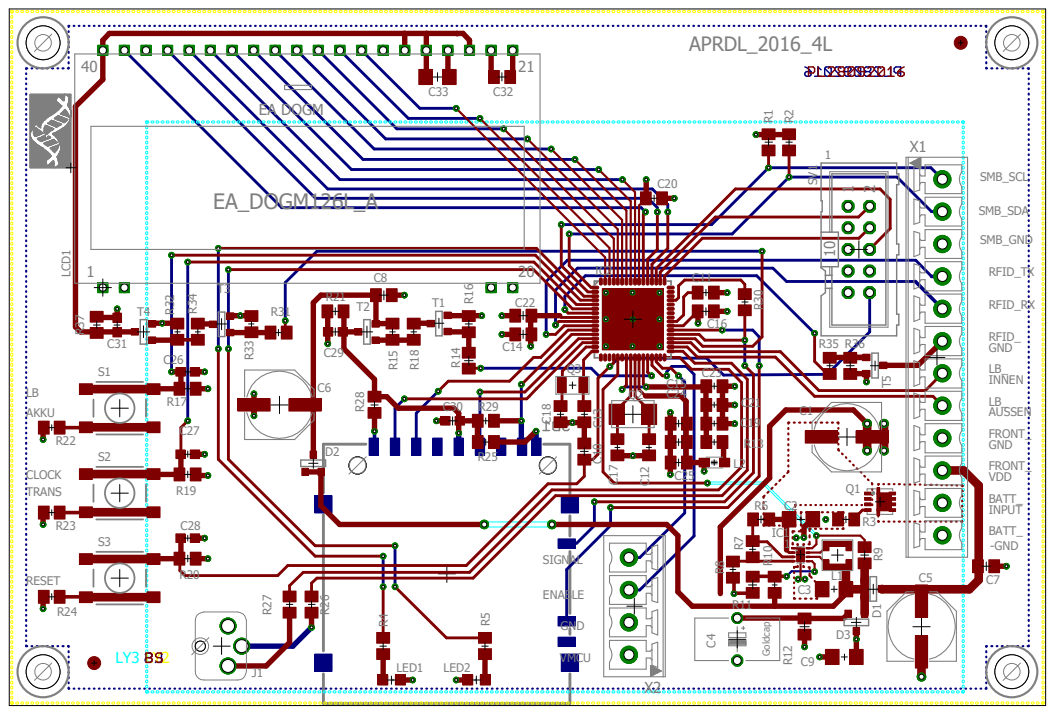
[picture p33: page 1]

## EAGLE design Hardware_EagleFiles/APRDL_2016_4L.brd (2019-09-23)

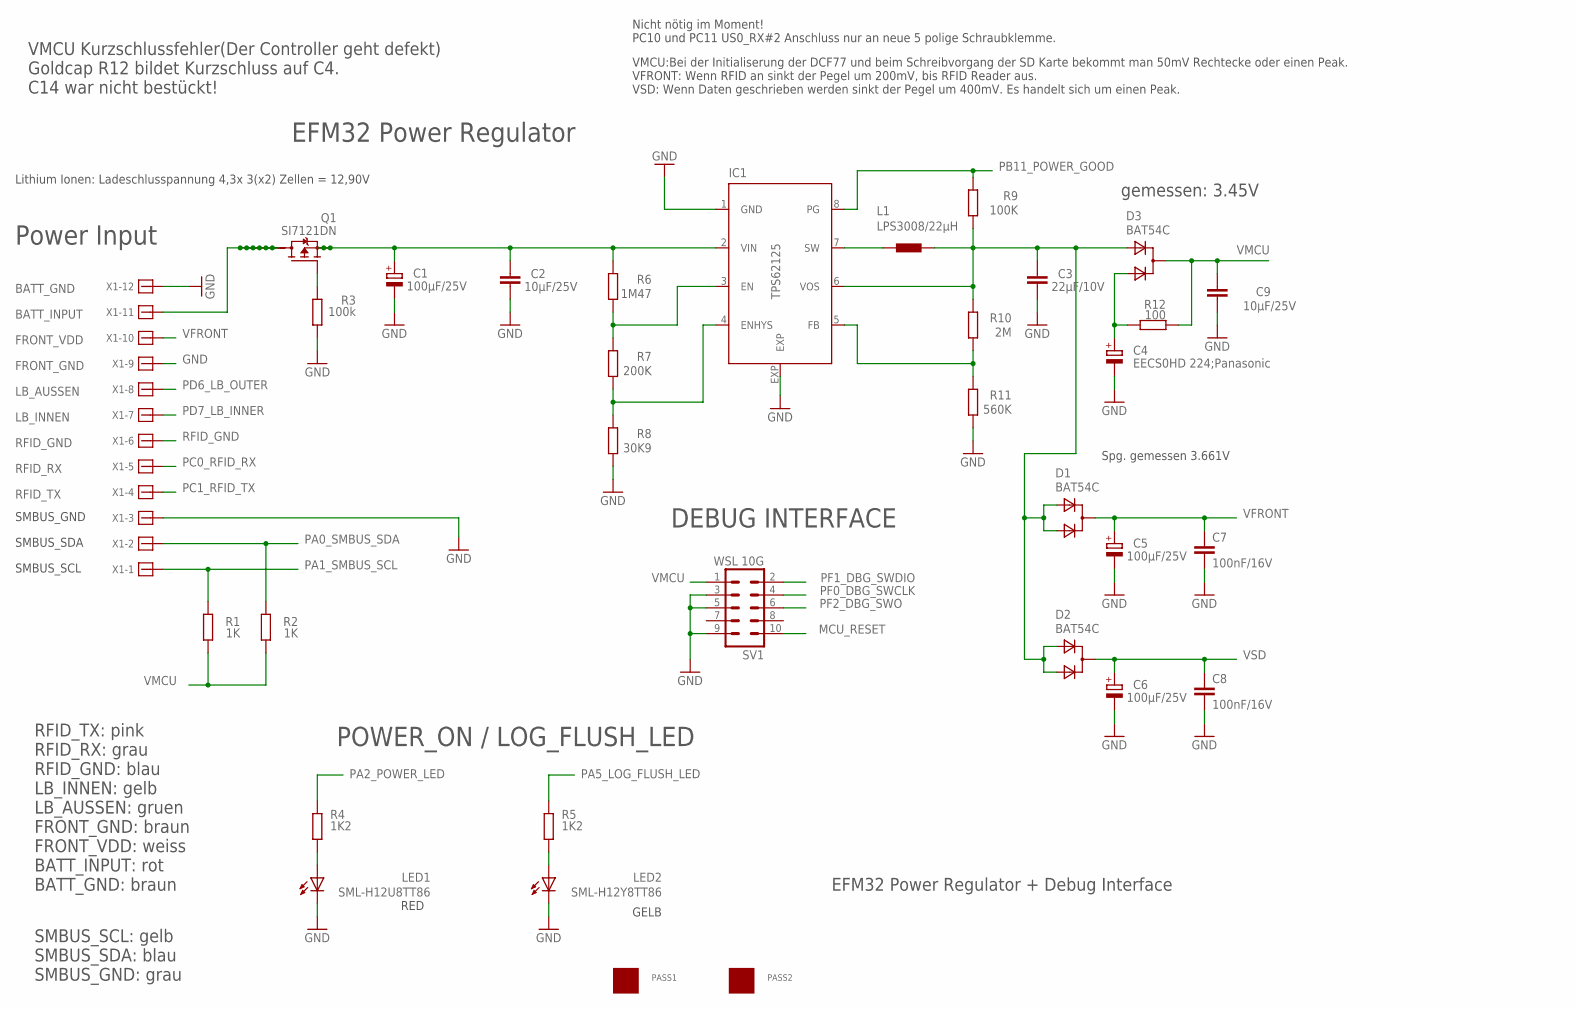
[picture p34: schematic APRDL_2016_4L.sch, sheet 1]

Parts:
C1, C5, C6: 100µF/25V; PANASONIC_E
C2, C9: 10µF/25V; C1206
C3: 22µF/10V; C1206
C4: EECS0HD 224;Panasonic; GOLDCAPSPK-V
C7, C8: 100nF/16V; C0805
D1, D2, D3: BAT54C; SOT-23@1
IC1: TPS62125; DSG_PWSO-N8_EXP
L1: LPS3008/22µH; LPS3008
LED1: SML-H12U8TT86; CHIPLED_0805
LED2: SML-H12Y8TT86; CHIPLED_0805
PASS1, PASS2: ROUND_1MM1.5; ROUND2_1.5MM
Q1: SI7121DN; TRANSISTOR-FET_1212-8S
R1, R2: 1K; R0805
R3: 100k; R0805
R4, R5: 1K2; R0805
R6: 1M47; R0805
R7: 200K; R0805
R8: 30K9; R0805
R9: 100K; R0805
R10: 2M; R0805
R11: 560K; R0805
R12: 100; R0805
SV1: WSL 10G; ML10
X1: 1803523

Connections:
BATT_INPUT: Q1.5 (D), Q1.6 (D), Q1.7 (D), Q1.8 (D), Q1.9 (D), Q1.10 (D), Q1.11 (D), X1.11
GND: C1.-, C2.2, C3.2, C4.-, C5.-, C6.-, C7.2, C8.2, C9.1, IC1.1 (GND), IC1.EXP, LED1.C, LED2.C, R3.1, R8.1, R11.1, SV1.3, SV1.5, SV1.9, X1.3, X1.9, X1.12; also elsewhere on the board
MCU_RESET: SV1.10; also elsewhere on the board
unnamed: IC1.3 (EN), R6.1, R7.2
unnamed: IC1.4 (ENHYS), R7.1, R8.2
unnamed: IC1.7 (SW), L1.1
unnamed: C1.+, C2.1, IC1.2 (VIN), Q1.1 (S), Q1.2 (S), Q1.3 (S), R6.2
unnamed: LED2.A, R5.2
unnamed: IC1.5 (FB), R10.1, R11.2
unnamed: Q1.4 (G), R3.2
unnamed: C4.+, D3.2 (A1), R12.2
unnamed: LED1.A, R4.2
PA0_SMBUS_SDA: R2.2, X1.2; also elsewhere on the board
PA1_SMBUS_SCL: R1.2, X1.1; also elsewhere on the board
PA2_POWER_LED: R4.1; also elsewhere on the board
PA5_LOG_FLUSH_LED: R5.1; also elsewhere on the board
PB11_POWER_GOOD: IC1.8 (PG), R9.2; also elsewhere on the board
PC0_RFID_RX: X1.5; also elsewhere on the board
PC1_RFID_TX: X1.4; also elsewhere on the board
PD6_LB_OUTER: X1.8; also elsewhere on the board
PD7_LB_INNER: X1.7; also elsewhere on the board
PF0_DBG_SWCLK: SV1.4; also elsewhere on the board
PF1_DBG_SWDIO: SV1.2; also elsewhere on the board
PF2_DBG_SWO: SV1.6; also elsewhere on the board
RFID_GND: X1.6; also elsewhere on the board
V1: C3.1, D1.2 (A1), D1.3 (A2), D2.2 (A1), D2.3 (A2), D3.3 (A2), IC1.6 (VOS), L1.2, R9.1, R10.2
VFRONT: C5.+, C7.1, D1.1 (C), X1.10
VMCU: C9.2, D3.1 (C), R1.1, R2.1, R12.1, SV1.1; also elsewhere on the board
VSD: C6.+, C8.1, D2.1 (C); also elsewhere on the board

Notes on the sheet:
BATT_GND
Lithium Ionen: Ladeschlusspannung 4,3x 3(x2) Zellen = 12,90V
BATT_INPUT
EFM32 Power Regulator + Debug Interface
Power Input
Spg. gemessen 3.661V
LB_AUSSEN
LB_INNEN
RFID_GND
SMBUS_SCL
SMBUS_SDA
SMBUS_GND
EFM32 Power Regulator
RFID_RX
RFID_TX
DEBUG INTERFACE
POWER_ON / LOG_FLUSH_LED
FRONT_VDD
FRONT_GND
GELB
RED
gemessen: 3.45V
RFID_TX: pink RFID_RX: grau RFID_GND: blau LB_INNEN: gelb LB_AUSSEN: gruen FRONT_GND: braun FRONT_VDD: weiss BATT_INPUT: rot BATT_GND: braun
SMBUS_SCL: gelb SMBUS_SDA: blau SMBUS_GND: grau
Nicht nötig im Moment! PC10 und PC11 US0_RX#2 Anschluss nur an neue 5 polige Schraubklemme.
VMCU:Bei der Initialiserung der DCF77 und beim Schreibvorgang der SD Karte bekommt man 50mV Rechtecke oder einen Peak. VFRONT: Wenn RFID an sinkt der Pegel um 200mV, bis RFID Reader aus. VSD: Wenn Daten geschrieben werden sinkt der Pegel um 400mV. Es handelt sich um einen Peak.
VMCU Kurzschlussfehler(Der Controller geht defekt) Goldcap R12 bildet Kurzschluss auf C4. C14 war nicht bestückt!

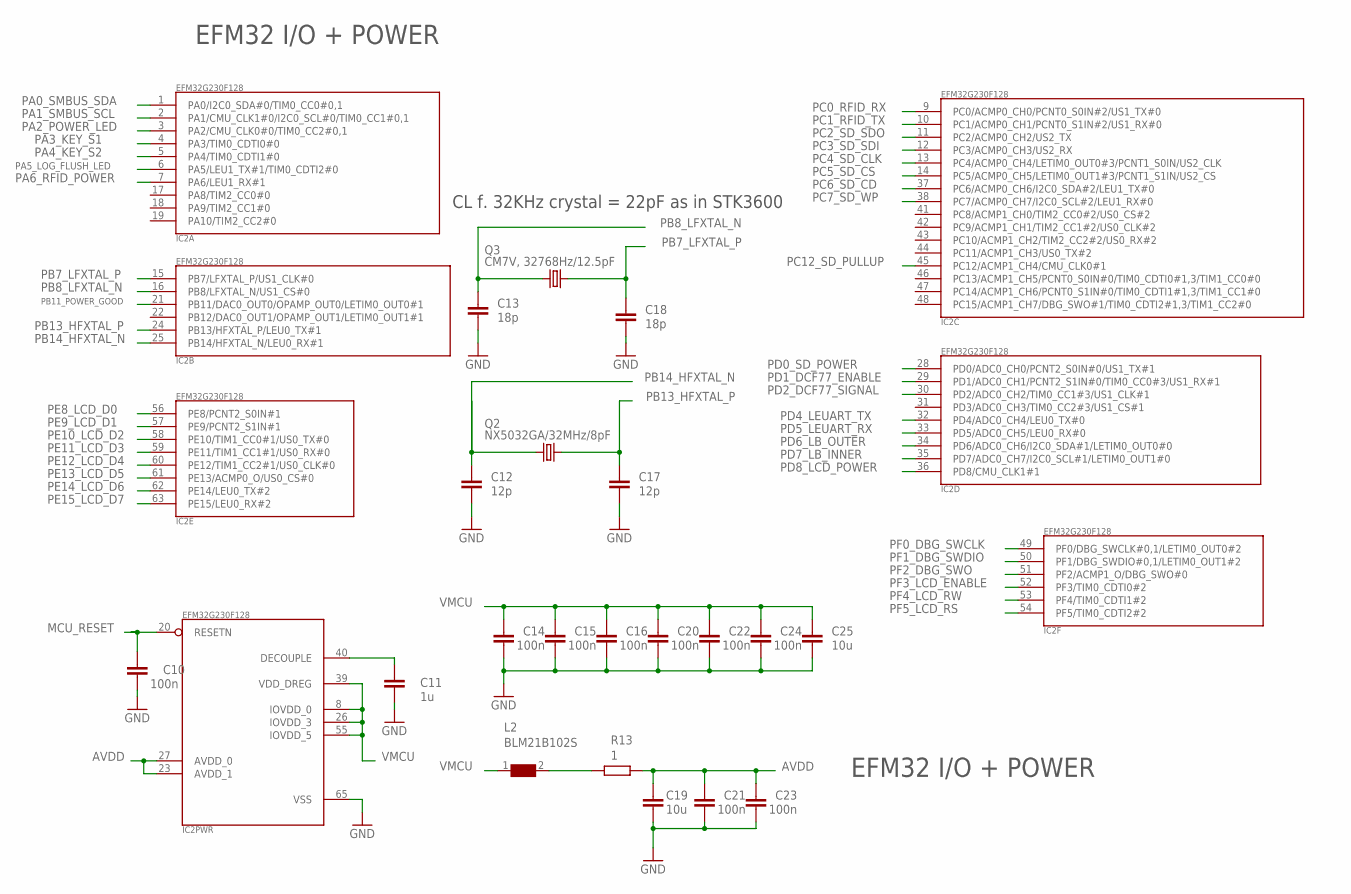
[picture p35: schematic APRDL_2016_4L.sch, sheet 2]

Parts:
C10, C14, C15, C16, C20, C21, C22, C23, C24: 100n; C0805
C11: 1u; C0805
C12, C17: 12p; C0805
C13, C18: 18p; C0805
C19, C25: 10u; C0805
IC2: EFM32G230F128; QFN64
L2: BLM21B102S; 0805
Q2: NX5032GA/32MHz/8pF; CRYSTAL2P5.0X3.2
Q3: CM7V, 32768Hz/12.5pF; CRYSTAL2P3.2X1.5
R13: 1; R0805

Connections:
AVDD: C19.2, C21.2, C23.2, IC2.23 (AVDD_1), IC2.27 (AVDD_0), R13.2
GND: C10.1, C11.1, C12.1, C13.1, C14.1, C15.1, C16.1, C17.1, C18.1, C19.1, C20.1, C21.1, C22.1, C23.1, C24.1, C25.1, IC2.65 (VSS); also elsewhere on the board
MCU_RESET: C10.2, IC2.20 (RESETN); also elsewhere on the board
unnamed: L2.2, R13.1
unnamed: C11.2, IC2.40 (DECOUPLE)
PA0_SMBUS_SDA: IC2.1 (PA0/I2C0_SDA#0/TIM0_CC0#0,1); also elsewhere on the board
PA1_SMBUS_SCL: IC2.2 (PA1/CMU_CLK1#0/I2C0_SCL#0/TIM0_CC1#0,1); also elsewhere on the board
PA2_POWER_LED: IC2.3 (PA2/CMU_CLK0#0/TIM0_CC2#0,1); also elsewhere on the board
PA3_KEY_S1: IC2.4 (PA3/TIM0_CDTI0#0); also elsewhere on the board
PA4_KEY_S2: IC2.5 (PA4/TIM0_CDTI1#0); also elsewhere on the board
PA5_LOG_FLUSH_LED: IC2.6 (PA5/LEU1_TX#1/TIM0_CDTI2#0); also elsewhere on the board
PA6_RFID_POWER: IC2.7 (PA6/LEU1_RX#1); also elsewhere on the board
PB7_LFXTAL_P: C18.2, IC2.15 (PB7/LFXTAL_P/US1_CLK#0), Q3.2
PB8_LFXTAL_N: C13.2, IC2.16 (PB8/LFXTAL_N/US1_CS#0), Q3.1
PB11_POWER_GOOD: IC2.21 (PB11/DAC0_OUT0/OPAMP_OUT0/LETIM0_OUT0#1); also elsewhere on the board
PB13_HFXTAL_P: C17.2, IC2.24 (PB13/HFXTAL_P/LEU0_TX#1), Q2.2
PB14_HFXTAL_N: C12.2, IC2.25 (PB14/HFXTAL_N/LEU0_RX#1), Q2.1
PC0_RFID_RX: IC2.9 (PC0/ACMP0_CH0/PCNT0_S0IN#2/US1_TX#0); also elsewhere on the board
PC1_RFID_TX: IC2.10 (PC1/ACMP0_CH1/PCNT0_S1IN#2/US1_RX#0); also elsewhere on the board
PC2_SD_SDO: IC2.11 (PC2/ACMP0_CH2/US2_TX); also elsewhere on the board
PC3_SD_SDI: IC2.12 (PC3/ACMP0_CH3/US2_RX); also elsewhere on the board
PC4_SD_CLK: IC2.13 (PC4/ACMP0_CH4/LETIM0_OUT0#3/PCNT1_S0IN/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); also elsewhere on the board
PC5_SD_CS: IC2.14 (PC5/ACMP0_CH5/LETIM0_OUT1#3/PCNT1_S1IN/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); also elsewhere on the board
PC6_SD_CD: IC2.37 (PC6/ACMP0_CH6/I2C0_SDA#2/LEU1_TX#0); also elsewhere on the board
PC7_SD_WP: IC2.38 (PC7/ACMP0_CH7/I2C0_SCL#2/LEU1_RX#0); also elsewhere on the board
PC12_SD_PULLUP: IC2.45 (PC12/ACMP1_CH4/CMU_CLK0#1); also elsewhere on the board
PD0_SD_POWER: IC2.28 (PD0/ADC0_CH0/PCNT2_S0IN#0/US1_TX#1); also elsewhere on the board
PD1_DCF77_ENABLE: IC2.29 (PD1/ADC0_CH1/PCNT2_S1IN#0/TIM0_CC0#3/US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); also elsewhere on the board
PD2_DCF77_SIGNAL: IC2.30 (PD2/ADC0_CH2/TIM0_CC1#3/US1_CLK#1); also elsewhere on the board
PD4_LEUART_TX: IC2.32 (PD4/ADC0_CH4/LEU0_TX#0); also elsewhere on the board
PD5_LEUART_RX: IC2.33 (PD5/ADC0_CH5/LEU0_RX#0); also elsewhere on the board
PD6_LB_OUTER: IC2.34 (PD6/ADC0_CH6/I2C0_SDA#1/LETIM0_OUT0#0); also elsewhere on the board
PD7_LB_INNER: IC2.35 (PD7/ADC0_CH7/I2C0_SCL#1/LETIM0_OUT1#0); also elsewhere on the board
PD8_LCD_POWER: IC2.36 (PD8/CMU_CLK1#1); also elsewhere on the board
PE8_LCD_D0: IC2.56 (PE8/PCNT2_S0IN#1); also elsewhere on the board
PE9_LCD_D1: IC2.57 (PE9/PCNT2_S1IN#1); also elsewhere on the board
PE10_LCD_D2: IC2.58 (PE10/TIM1_CC0#1/US0_TX#0); also elsewhere on the board
PE11_LCD_D3: IC2.59 (PE11/TIM1_CC1#1/US0_RX#0); also elsewhere on the board
PE12_LCD_D4: IC2.60 (PE12/TIM1_CC2#1/US0_CLK#0); also elsewhere on the board
PE13_LCD_D5: IC2.61 (PE13/ACMP0_O/US0_CS#0); also elsewhere on the board
PE14_LCD_D6: IC2.62 (PE14/LEU0_TX#2); also elsewhere on the board
PE15_LCD_D7: IC2.63 (PE15/LEU0_RX#2); also elsewhere on the board
PF0_DBG_SWCLK: IC2.49 (PF0/DBG_SWCLK#0,1/LETIM0_OUT0#2); also elsewhere on the board
PF1_DBG_SWDIO: IC2.50 (PF1/DBG_SWDIO#0,1/LETIM0_OUT1#2); also elsewhere on the board
PF2_DBG_SWO: IC2.51 (PF2/ACMP1_O/DBG_SWO#0); also elsewhere on the board
PF3_LCD_ENABLE: IC2.52 (PF3/TIM0_CDTI0#2); also elsewhere on the board
PF4_LCD_RW: IC2.53 (PF4/TIM0_CDTI1#2); also elsewhere on the board
PF5_LCD_RS: IC2.54 (PF5/TIM0_CDTI2#2); also elsewhere on the board
VMCU: C14.2, C15.2, C16.2, C20.2, C22.2, C24.2, C25.2, IC2.8 (IOVDD_0), IC2.26 (IOVDD_3), IC2.39 (VDD_DREG), IC2.55 (IOVDD_5), L2.1; also elsewhere on the board

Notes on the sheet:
EFM32 I/O + POWER
CL f. 32KHz crystal = 22pF as in STK3600

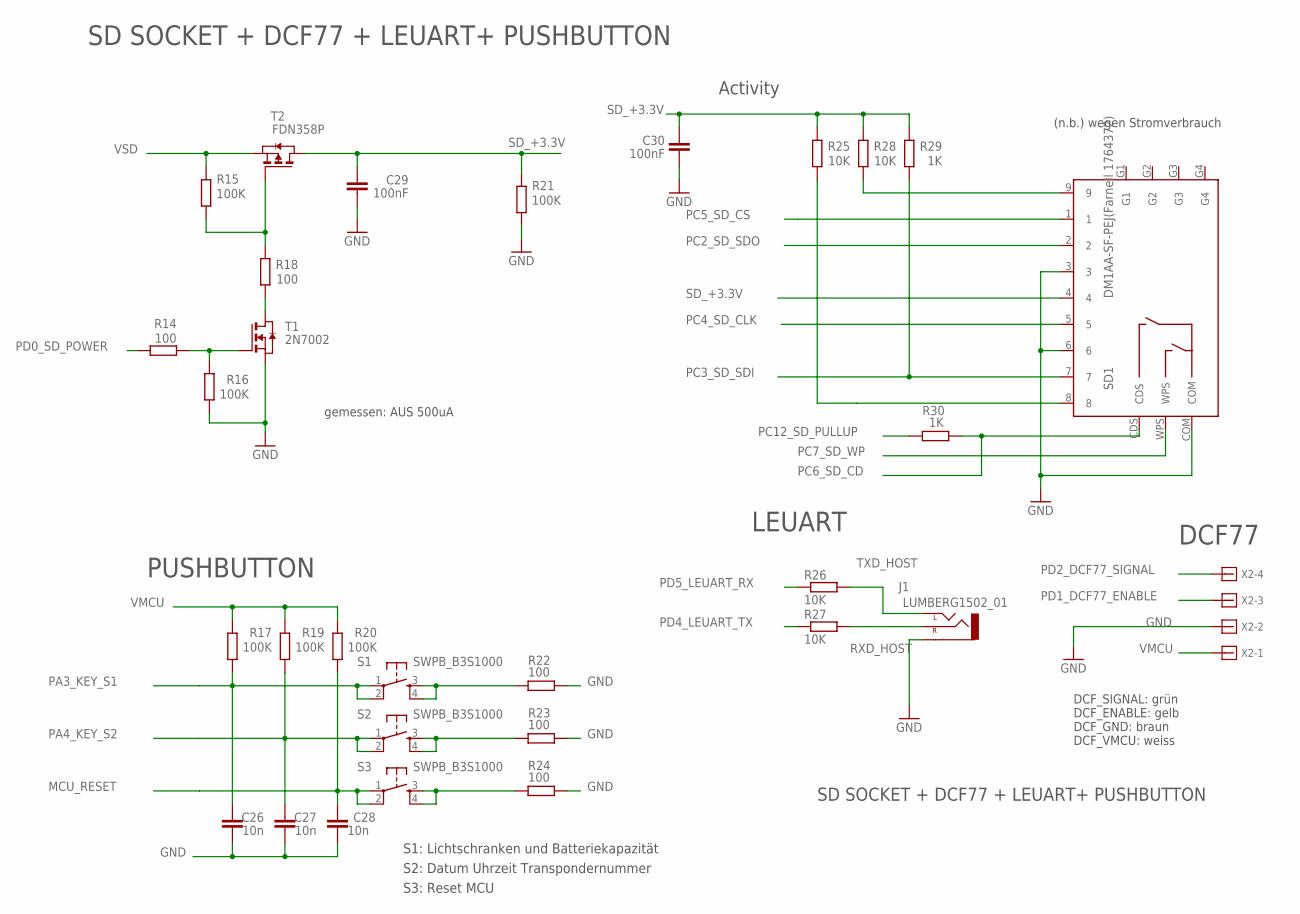
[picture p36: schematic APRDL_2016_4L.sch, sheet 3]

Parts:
C26, C27, C28: 10n; C0603
C29, C30: 100nF; C0603
J1: LUMBERG1502_01
R14, R18, R22, R23, R24: 100; R0805
R15, R16, R17, R19, R20, R21: 100K; R0805
R25, R26, R27, R28: 10K; R0805
R29, R30: 1K; R0805
S1, S2, S3: SWPB_B3S1000; DTSM-6
SD1: DM1AA-SF-PEJ(Farnell 1764372); DM1AA-SF-PEJ
T1: 2N7002; ZETEX_SOT-23
T2: FDN358P; ZETEX_SOT-23
X2: 1803442

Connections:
GND: C26.1, C27.1, C28.1, C29.2, C30.2, J1.P$1 (1-SLEEVE), R16.1, R21.1, R22.2, R23.2, R24.2, SD1.3, SD1.6, SD1.COM, T1.2 (S), X2.2; also elsewhere on the board
MCU_RESET: C28.2, R20.1, S3.1, S3.2; also elsewhere on the board
unnamed: R15.1, R18.2, T2.3 (G)
unnamed: R18.1, T1.1 (D)
unnamed: R14.1, R16.2, T1.3 (G)
unnamed: R28.1, SD1.9
unnamed: R25.1, SD1.8
unnamed: R22.1, S1.3, S1.4
unnamed: R23.1, S2.3, S2.4
unnamed: R24.1, S3.3, S3.4
PA3_KEY_S1: C26.2, R17.1, S1.1, S1.2; also elsewhere on the board
PA4_KEY_S2: C27.2, R19.1, S2.1, S2.2; also elsewhere on the board
PC2_SD_SDO: SD1.2; also elsewhere on the board
PC3_SD_SDI: R29.1, SD1.7; also elsewhere on the board
PC4_SD_CLK: SD1.5; also elsewhere on the board
PC5_SD_CS: SD1.1; also elsewhere on the board
PC6_SD_CD: R30.1, SD1.CDS; also elsewhere on the board
PC7_SD_WP: SD1.WPS; also elsewhere on the board
PC12_SD_PULLUP: R30.2; also elsewhere on the board
PD0_SD_POWER: R14.2; also elsewhere on the board
PD1_DCF77_ENABLE: X2.3; also elsewhere on the board
PD2_DCF77_SIGNAL: X2.4; also elsewhere on the board
PD4_LEUART_TX: R27.1; also elsewhere on the board
PD5_LEUART_RX: R26.1; also elsewhere on the board
RXD_HOST: J1.P$3 (3-RIGHT), R27.2
SD_+3.3V: C29.1, C30.1, R21.2, R25.2, R28.2, R29.2, SD1.4, T2.1 (D)
TXD_HOST: J1.P$2 (2-LEFT), R26.2
VMCU: R17.2, R19.2, R20.2, X2.1; also elsewhere on the board
VSD: R15.2, T2.2 (S); also elsewhere on the board

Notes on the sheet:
LEUART
gemessen: AUS 500uA
DCF77
Activity
PUSHBUTTON
SD SOCKET + DCF77 + LEUART+ PUSHBUTTON
S1: Lichtschranken und Batteriekapazität
S2: Datum Uhrzeit Transpondernummer
S3: Reset MCU
(n.b.) wegen Stromverbrauch
DCF_SIGNAL: grün DCF_ENABLE: gelb DCF_GND: braun DCF_VMCU: weiss

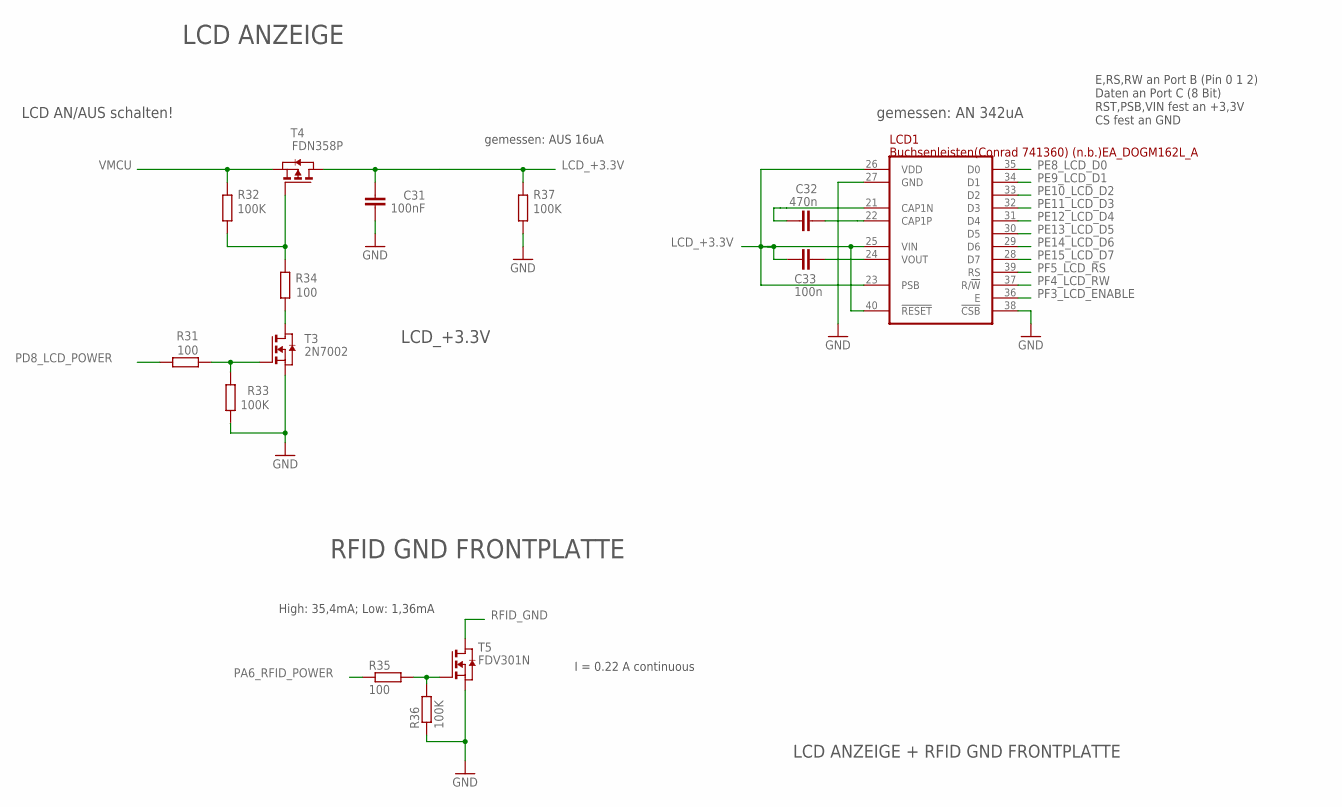
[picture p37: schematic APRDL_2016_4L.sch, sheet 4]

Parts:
C31: 100nF; C0603
C32: 470n; C0805
C33: 100n; C1206
LCD1: Buchsenleisten(Conrad 741360) (n.b.)EA_DOGM162L_A; EA_DOGM
R31, R34, R35: 100; R0805
R32, R33, R36, R37: 100K; R0805
T3: 2N7002; ZETEX_SOT-23
T4: FDN358P; ZETEX_SOT-23
T5: FDV301N; SOT-23

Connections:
GND: C31.2, LCD1.27 (GND), LCD1.38 (!CSB!), R33.1, R36.1, R37.1, T3.2 (S), T5.2 (S); also elsewhere on the board
LCD_+3.3V: C31.1, C33.2, LCD1.23 (PSB), LCD1.25 (VIN), LCD1.26 (VDD), LCD1.40 (!RESET!), R37.2, T4.1 (D)
unnamed: R35.2, R36.2, T5.3 (G)
unnamed: R32.1, R34.2, T4.3 (G)
unnamed: R34.1, T3.1 (D)
unnamed: R31.1, R33.2, T3.3 (G)
unnamed: C32.2, LCD1.22 (CAP1P)
unnamed: C32.1, LCD1.21 (CAP1N)
unnamed: C33.1, LCD1.24 (VOUT)
PA6_RFID_POWER: R35.1; also elsewhere on the board
PD8_LCD_POWER: R31.2; also elsewhere on the board
PE8_LCD_D0: LCD1.35 (D0); also elsewhere on the board
PE9_LCD_D1: LCD1.34 (D1); also elsewhere on the board
PE10_LCD_D2: LCD1.33 (D2); also elsewhere on the board
PE11_LCD_D3: LCD1.32 (D3); also elsewhere on the board
PE12_LCD_D4: LCD1.31 (D4); also elsewhere on the board
PE13_LCD_D5: LCD1.30 (D5); also elsewhere on the board
PE14_LCD_D6: LCD1.29 (D6); also elsewhere on the board
PE15_LCD_D7: LCD1.28 (D7); also elsewhere on the board
PF3_LCD_ENABLE: LCD1.36 (E); also elsewhere on the board
PF4_LCD_RW: LCD1.37 (R/!W!); also elsewhere on the board
PF5_LCD_RS: LCD1.39 (RS); also elsewhere on the board
RFID_GND: T5.1 (D); also elsewhere on the board
VMCU: R32.2, T4.2 (S); also elsewhere on the board

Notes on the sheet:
LCD ANZEIGE + RFID GND FRONTPLATTE
High: 35,4mA; Low: 1,36mA
RFID GND FRONTPLATTE
LCD ANZEIGE
E,RS,RW an Port B (Pin 0 1 2) Daten an Port C (8 Bit) RST,PSB,VIN fest an +3,3V CS fest an GND
gemessen: AUS 16uA
LCD_+3.3V
LCD AN/AUS schalten!
gemessen: AN 342uA
I = 0.22 A continuous

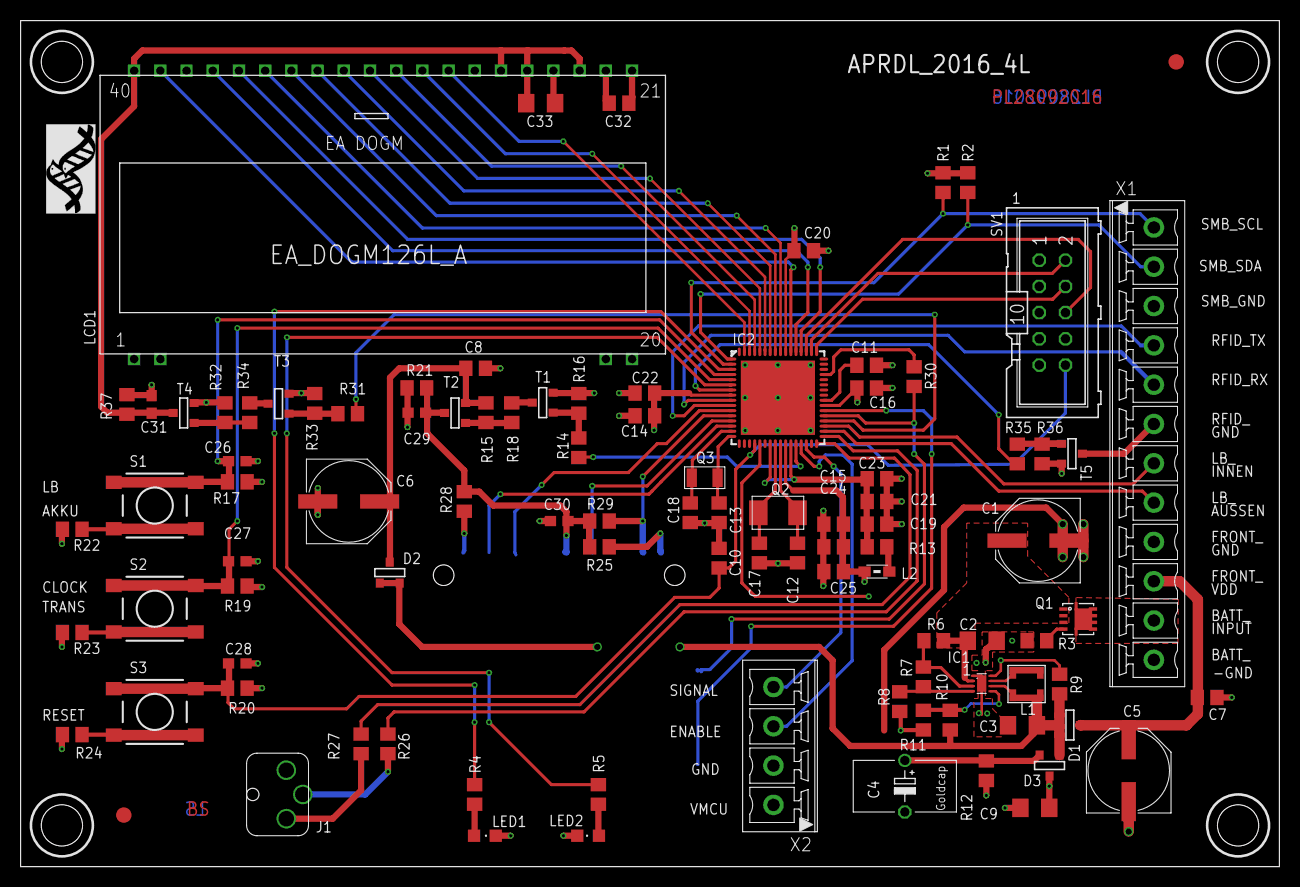
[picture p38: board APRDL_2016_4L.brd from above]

Board: 4 copper layers, 122.0 x 82.0 mm, 99 parts (1 on the bottom side), 82 nets.

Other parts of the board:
U$2: MPIO-ICON

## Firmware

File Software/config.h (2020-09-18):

/***************************************************************************//**
 * @file
 * @brief	Project configuration file
 * @author	Ralf Gerhauser
 * @version	2016-02-27
 *
 * This file allows to set miscellaneous configuration parameters.  It must be
 * included by all modules.
 *
 ****************************************************************************//*
Revision History:
2016-02-26,rage	Increased LOG_BUF_SIZE to 4KB.
2016-02-10,rage	Set RFID_POWER_OFF_TIMEOUT to 6 minutes.
2014-11-11,rage	Derived from project "AlarmClock".
*/

#ifndef __INC_config_h
#define __INC_config_h

/*=============================== Header Files ===============================*/

#include <stdio.h>
#include <stdbool.h>
#include "em_device.h"

/*=============================== Definitions ================================*/

/*
 * Basic defines - should all be moved to Generic.h
 */
    /* terminators for lists and strings */

#define	EOL		NULL		/* EndOfList		*/
#define EOS		'\0'		/* EndOfString		*/
#define	NONE		(-1)

    /* macro to calculate the number of elements of an array */
#define ELEM_CNT(array)  (sizeof (array) / sizeof ((array)[0]))

/*
 * LED Definitions for this project
 */
    /*!@brief GPIO Port of the (red) Power-LED. */
#define POWER_LED_PORT		gpioPortA
    /*!@brief GPIO Pin of the (red) Power-LED. */
#define POWER_LED_PIN		2
    /*! @brief Macro to set or clear the Power-LED */
#define POWER_LED   IO_Bit(GPIO->P[POWER_LED_PORT].DOUT, POWER_LED_PIN)
    /*!@brief GPIO Port of the (green) Log Flush LED. */
#define LOG_FLUSH_LED_PORT	gpioPortA
    /*!@brief GPIO Pin of the (green) Log Flush LED. */
#define LOG_FLUSH_LED_PIN	5		//! State: 0=OFF, 1=ON
    /*! @brief Macro to set or clear the Log Flush LED */
#define LOG_FLUSH_LED IO_Bit(GPIO->P[LOG_FLUSH_LED_PORT].DOUT, LOG_FLUSH_LED_PIN)

/*!
 * @brief MPU Clock Configuration.
 *
 * Set to 0 to use the internal RC oscillator, if 1 the external 32MHz XTAL
 * is used.
 */
#define USE_EXT_32MHZ_CLOCK	0

/*
 * Configuration for module "AlarmClock"
 */
    /*!@brief RTC frequency in [Hz]. */
#define RTC_COUNTS_PER_SEC	32768


/*!
 * @brief Interrupt Priority Settings
 *
 * There are 8 priority levels 0 to 7 with 0 to be the highest and 7 to be the
 * lowest priority.  DCF77 (which is called from the EXTI handler) and RTC must
 * use the same priority level to lock-out each other, because they both use
 * function localtime() and this is not multithreading save.  Funktion
 * localtime_r() would be the right choice here, unfortunately it is not
 * available with the IAR compiler library.
 */
#define INT_PRIO_UART	2		//!< UART interrupts for the RFID reader
#define INT_PRIO_LEUART	2		//!< LEUART RX interrupt (not used)
#define INT_PRIO_DMA	2		//!< DMA is used for LEUART
#define INT_PRIO_SMB	2		//!< SMBus used by the battery monitor
#define INT_PRIO_RTC	3		//!< lower priority than others
#define INT_PRIO_EXTI	INT_PRIO_RTC	//!< must be the same as @ref INT_PRIO_RTC


/*
 * Configuration for Atomic Clock module "DCF77.c"
 */
    /*!@brief Use Hardware Enable pin of the DCF77 receiver. */
#define DCF77_HARDWARE_ENABLE	1

    /*!@brief Activate DCF77 only once per day. */
#define DCF77_ONCE_PER_DAY	1

    /*!@brief Call ShowDCF77Indicator() to flash red LED on DCF77 signal. */
#define DCF77_INDICATOR		1


/*
 * Configuration for module "RFID"
 */

    /*!@brief Time in [s] after which the RFID reader is powered-off. */
#define RFID_POWER_OFF_TIMEOUT	360	// 6min


/*
 * Configuration for module "Logging"
 */
    /*!@brief Size of the log buffer in bytes. */
#define LOG_BUF_SIZE	4096

    /*!@brief Use this define to specify a function to be called for monitoring
     * the log activity.  Here, monitoring is done via the LEUART interface.
     */
#define LOG_MONITOR_FUNCTION	drvLEUART_puts

/* forward declaration */
void    drvLEUART_puts(const char *str);

    /*!@brief Disable "alive" message by setting this interval to 0. */
#define LOG_ALIVE_INTERVAL	0


/*!@name DMA Channel Assignment
 *
 * The following definitions assign the 8 DMA channels to the respective
 * devices or drivers.  These defines are used as index within the global
 * @ref DMA_DESCRIPTOR_TypeDef structure @ref g_DMA_ControlBlock.
 */
//@{
#define DMA_CHAN_LEUART_RX	0	//! LEUART Rx uses DMA channel 0
#define DMA_CHAN_LEUART_TX	1	//! LEUART Tx uses DMA channel 1
//@}


/*================================== Macros ==================================*/

#ifdef DEBUG
    /*
     * Debugging output via ITM or LEUART
     */
    #if DEBUG_VIA_ITM
	#define DBG_PUTC(ch)	ITM_SendChar(ch)
	#define DBG_PUTS(str)	ITM_SendStr(str)
	uint32_t ITM_SendChar (uint32_t ch);
	void ITM_SendStr(const char *pStr);
    #else
	#define DBG_PUTC(ch)	drvLEUART_putc(ch)
	#define DBG_PUTS(str)	drvLEUART_puts(str)
	void	drvLEUART_putc(char ch);
	void	drvLEUART_puts(const char *str);
    #endif
    void dbgInit(void);
#else
    #define DBG_PUTC(ch)
    #define DBG_PUTS(str)
#endif

    /*! Macro to address a single bit in the I/O range (peripheral range) in
     *  an atomic manner.
     * @param address   I/O register address.
     * @param bitNum    Bit number within this register.
     */
#define IO_BIT_ADDR(address, bitNum)					\
	((__IO uint32_t *) (BITBAND_PER_BASE				\
			+ (((uint32_t)(address)) - PER_MEM_BASE) * 32	\
			+ (bitNum) * 4))

    /*! Shortcut to directly access an I/O-bit. */
#define IO_Bit(regName, bitNum)	*IO_BIT_ADDR(&regName, bitNum)

    /*! Macro to address a single bit in an SRAM variable in an atomic manner.
     * @param address   Address of the variable in SRAM.
     * @param bitNum    Bit number within this variable.
     */
#define SRAM_BIT_ADDR(address, bitNum)					\
	((__IO uint32_t *) (BITBAND_RAM_BASE				\
			+ (((uint32_t)(address)) - RAM_MEM_BASE) * 32	\
			+ (bitNum) * 4))

    /*! Shortcut to directly access a bit in a variable. */
#define Bit(varName, bitNum)	*SRAM_BIT_ADDR(&varName, bitNum)

/*=========================== Typedefs and Structs ===========================*/

/*!@brief Structure to hold Project Information */
typedef struct
{
    char const  ID[12];
    char const  Date[16];
    char const  Time[10];
    char const  Version[16];
} PRJ_INFO;


/*!@brief Enumeration of Alarm Identifiers
 *
 * This is the list of Alarm IDs used by this application.  They are used to
 * identify a particular alarm time entry via the <b>alarmNum</b> parameter
 * when calling alarm functions, e.g. AlarmSet().
 */
typedef enum
{
    ALARM_DCF77_WAKE_UP,    //!< Wake up DCF77 to synchronize the system clock
    ALARM_BATTERY_MON_1,    //!< Time #1 for logging battery status
    ALARM_BATTERY_MON_2,    //!< Time #2 for logging battery status
    END_ALARM_ID
} ALARM_ID;


/*!@brief Enumeration of the EM1 Modules
 *
 * This is the list of Software Modules that require EM1 to work, i.e. they
 * will not work in EM2 because clocks, etc. would be disabled.  These enums
 * are used to set/clear the appropriate bit in the @ref g_EM1_ModuleMask.
 */
typedef enum
{
    EM1_MOD_RFID,	//!<  0: The RFID Modules uses the UART
    END_EM1_MODULES
} EM1_MODULES;

/*======================== External Data and Routines ========================*/

extern volatile bool	 g_flgIRQ;		// Flag: Interrupt occurred
extern volatile uint16_t g_EM1_ModuleMask;	// Modules that require EM1


#endif /* __INC_config_h */

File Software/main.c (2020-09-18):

/***************************************************************************//**
 * @file
 * @brief	SNB Heaven
 * @author	Ralf Gerhauser
 * @version	2016-02-27
 *
 * This application consists of the following modules:
 * - ExtInt.c - External interrupt handler.
 * - Keys.c - Key interrupt handling and translation.
 * - AlarmClock.c - Alarm clock and timers facility.
 * - DCF77.c - DCF77 Atomic Clock Decoder
 * - clock.c - An implementation of the POSIX time() function.
 * - LCD_DOGM162.c - Driver for the DOGM162 LC-Display.
 * - Display.c - Display manager for LCD.
 * - LightBarrier.c - Interrupt logic for the outer and inner light barrier,
 *   enables the RFID reader.
 * - RFID.c - RFID reader to receive transponder IDs.
 * - BatteryMon.c - Battery monitor, periodically reads the state of the
 *   battery via the SMBus.
 * - LEUART.c - The Low-Energy UART can be used as monitoring and debugging
 *   connection to a host computer.
 * - microsd.c - Together with the files "diskio.c" and "ff.c", this module
 *   provides an implementation of a FAT file system on the SD-Card.
 * - Logging.c - Logging facility to send messages to the LEUART and store
 *   them into a file on the SD-Card.
 * - PowerFail.c - Handler to switch off all loads in case of Power Fail.
 *
 * Parts of the code are based on the example code of AN0006 "tickless calender"
 * from Energy Micro AS.
 *
 ***************************************************************************//**
 *
 * Parts are Copyright 2013 Energy Micro AS, http://www.energymicro.com
 *
 *******************************************************************************
 *
 * Permission is granted to anyone to use this software for any purpose,
 * including commercial applications, and to alter it and redistribute it
 * freely, subject to the following restrictions:
 *
 * 1. The origin of this software must not be misrepresented; you must not
 *    claim that you wrote the original software.
 * 2. Altered source versions must be plainly marked as such, and must not be
 *    misrepresented as being the original software.
 * 3. This notice may not be removed or altered from any source distribution.
 * 4. The source and compiled code may only be used on Energy Micro "EFM32"
 *    microcontrollers and "EFR4" radios.
 *
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
 * Energy Micro AS will not be liable for any consequential, incidental, or
 * special damages, or any other relief, or for any claim by any third party,
 * arising from your use of this Software.
 *
 ****************************************************************************//*
Revision History:
2020-09-18,rage	Version 1.2:
              - Added support for battery controller TI bq40z50.
                LogBatteryInfo: Removed SBS_ManufacturerData.
                Display SBS_RunTimeToEmpty in days/hours/min.
                Display SBS_SerialNumber as hex value.
              - Corrected decoding of Short-Range(SR) RFID Reader transponder ID
              - Added Power Fail Logic
              - Added Interrupt Priority Settings
2016-04-13,rage	Removed trigger mask from <l_ExtIntCfg>.
2016-02-27,rage	Changed project name to "APRDL".
2016-02-16,rage	Since ExtIntInit() no more enables the external interrupts,
		ExtIntEnableAll() has to be called afterwards.
		Reboot if "*.UPD" files have been found on SD-Card.
2015-05-11,rage	Finished code, completed documentation.
2014-11-11,rage	Initial version.
*/

/*!
 * @mainpage
 * <b>Description</b><br>
 * APRDL (code name SNB_Heaven) is an application to control an intelligent
 * nest box (SNB = Smart Nest Box).  It consists of the following components:
 *
 * <b>Microcontroller</b><br>
 * The heart of the board is an EFM32G230 microcontroller.  It provides two
 * different clock domains: All low-energy peripheral is clocked via a
 * 32.768kHz external XTAL.  The MCU and other high performance peripheral
 * uses a high-frequency clock.  The board can be configured to use the
 * internal RC-oscillator, or an external 32MHz XTAL for that purpose,
 * see define @ref USE_EXT_32MHZ_CLOCK.
 *
 * <b>DCF77 Atomic Clock</b><br>
 * When powered on, the DCF77 hardware module is enabled to receive the time
 * information and set the system clock.  During this phase, the Power-On LED
 * (i.e. LED1) shows the current state of the DCF signal.  The further behavior
 * depends on the settings in the <i>config.h</i> file.  If the define @ref
 * DCF77_ONCE_PER_DAY is 1, the receiver (and also the LED) will be switched
 * off after time has been synchronized.  As the name of the define suggests,
 * it will be switched on once per day.  To properly detect a change between
 * winter and summer time, i.e. <i>normal time</i> (MEZ) and <i>daylight saving
 * time</i> (MESZ), this happens at 01:55 for MEZ, and 02:55 for MESZ.<br>
 * If the define is 0, the receiver remains switched on, but the LED will only
 * get active again when the time signal gets out-of-sync.<br>
 *
 * <b>Light Barriers</b><br>
 * There is an inner and outer light barrier mounted on the front of the nest
 * box.  When activity is detected by one of the light barriers, the RFID
 * reader will be enabled.  The current state of the light barriers can be
 * viewed on the LC-Display by asserting the S1 button.
 *
 * <b>RFID Reader</b><br>
 * The RFID reader is used to receive the transponder number of the bird,
 * moving in or out of the nest box.  It is enabled by the light barriers
 * and shut down after @ref RFID_POWER_OFF_TIMEOUT seconds when there is no
 * more activity detected.
 *
 * <b>Keys (Push Buttons)</b><br>
 * There exist 3 push buttons on the board.  When asserted, the following
 * action will be taken:
 * - S1 displays the status of the light barriers (LBO is the outer, LBI the
 *   inner light barrier), and the battery voltage and remaining capacity.
 * - S2 displays the current date and time and the previously detected
 *   transponder number.  If this button is asserted for more than 5 seconds,
 *   the transponder number on the LCD will be cleared.
 * - S3 is the RESET button.
 *
 * The duration how long the respective information is displayed before
 * switching the LCD off again, can be adjusted by the define @ref
 * LCD_POWER_OFF_TIMEOUT.
 *
 * <b>LC-Display</b><br>
 * The display provides 2 lines á 16 characters.  It is connected to the
 * EFM32 microcontroller via a parallel bus interface.  To save power, the
 * whole display usually is switched off and only activated by asserting a
 * push button or exchanging the SD-Card.  However, after a power-up or reset,
 * the LCD remains powered on until the system clock is synchronized with
 * the DCF77 atomic clock signal.  This allows the user to read the firmware
 * version, the free space on the SD-Card, and the log filename.
 *
 * The visual contrast of the LCD can be adjusted via @ref l_Contrast.
 *
 * <b>LEDs</b><br>
 * There are two LEDs, one is red, the other one is green.
 * - The red LED is the Power-On LED.  It shows the current state of the
 *   DCF77 signal during receiving of the time information.  In normal
 *   condition the LED will be switched off.
 * - The green LED is the Log Flush LED.  It flashes whenever there are write
 *   accesses to SD-Card.
 *
 * <b>SD-Card</b><br>
 * The SD-Card is used to store logging information.  Only formatted cards
 * can be used, supported file systems are FAT12, FAT16, and FAT32.  The
 * filenames must follow the DOS schema 8+3, i.e. maximum 8 characters for
 * the basename, and 3 for the extension.  If the SD-Card contains a file
 * <b>BOX<i>nnnn</i>.TXT</b>, where <b><i>nnnn</i></b> can be any decimal
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

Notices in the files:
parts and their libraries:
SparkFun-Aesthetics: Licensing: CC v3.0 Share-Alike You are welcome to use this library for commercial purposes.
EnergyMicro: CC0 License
